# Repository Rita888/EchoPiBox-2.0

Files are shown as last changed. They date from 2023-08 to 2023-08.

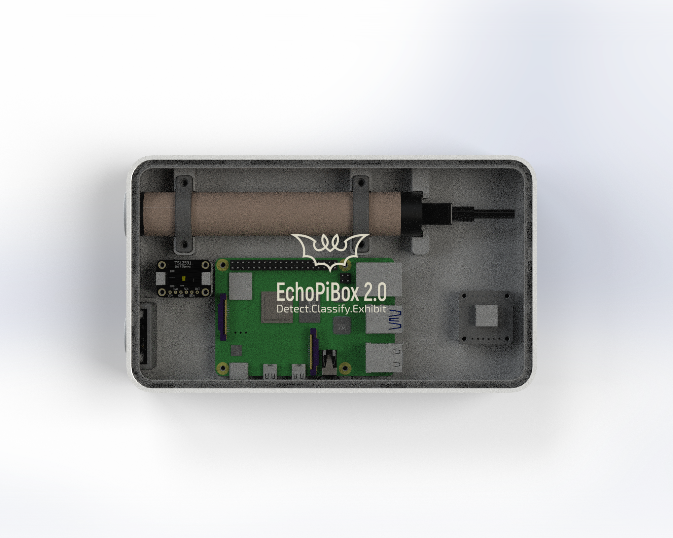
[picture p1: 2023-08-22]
Rita Enclosure V1/Render (2).png

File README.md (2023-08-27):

# EchoBoxPi2.0

Detect.Classify.Exhibit



EchoPiBox 2.0 Passive Acoustic Monitor: Detection, Species Identification Accuracy and Displaying Real Time Data.

MSc Connected Environments Dissertation by Margarita Smoldareva

Research Question: Can Raspberry Pi 4 host open-source machine learning model and three additional sensors to classify social bat calls plus display environmental variables along with accurate bat species in real time using Flutter App? 

This study is part of MSc Connected Environments programme which explores the use of a microprocessor and other hardware components wired together in a box with ability to detect and classify bats using open-source machine learning model developed by University College London (UCL). The aims and objectives of this thesis report are noted below that indicated the flow of the project. 

Detect
Aim: - Build a physical device (EchoPiBox 2.0) which allows bat calls detection. 
Objective: Set up Raspberry Pi 4, Ultramic, Temperature/Humidity and GPS Sensors to record environmental variables and bat calls. 

Classify
Aim: - Deploy Machine Learning Algorithm on EchoPiBox 2.0 and test its accuracy. 
Objective: Select and deploy the device across five sites based in England and Wales to test accuracy of classification of bat calls. 

Exhibit
Aim: - Display the Real Time Data
Objective: Using Flutter App display data collected by EchoPiBox 2.0 when deployed at any time.


Flowchart 1: Proposed Scheme for Deployment

UK bats and their importance 
Bat, being the sole flying mammal of the world is the most diverse specie on Earth. Except for Antarctica, they are found on every continent. 
In the United Kingdom, 18 different breeds of bat along with some vagrant visitors are found (Entwhistle et al., 2001). Bats are important creatures whose ecological 
roles as predator and prey have been postulated to regulate environmental and economic services including nutrient distribution, arthropod suppression, pollination, 
and biodiversity. For the purpose of foraging and roosting, the utilisation of different habitats by bats regulates nutrient dispersion and soil fertility to
facilitate dietary transfer within ecosystems from nutrient-rich locations to poor-nutrient regions (Buchler, 1975). Furthermore, bats serve as exceptional 
ecological indicators of habitat quality. Due to their mobility, ecological distribution, population trends, taxonomic stability, size, global distribution, 
and longevity, bats have great potential as bioindicators for contaminants and disturbance in the atmosphere (Kasso and Balakrishnan, 2013, 4). 

Similarly, tropical bats provide immense support as pollinators to national and local economies. The role of bats as a bioindicator taxa is highly essential to
evaluate climatic responses, loss of habitat, and insects’ population in a particular region enabling the researchers to reflect on forthcoming impacts and 
wider-scale changes on biodiversity.

Despite being an essential contributor to the environment and nature, bat populations have drastically declined in the United Kingdom. Due to a lack of substantial 
historical data on bat distribution and population sizes, it is hard to quantify the population decline. However, some common issues for bats' survival include poor 
management of their feeding habitats, roost sites, and lack of protection of hibernation sites (hibernacula) (Entwhistle, 7). Thus, the population of British bats
has shrunk notably and species conservation techniques and interventions are being studied and implemented to meet their habitat requirements (Hill and Greenaway, 2008).

Bat Conservation Trust (BCT, 2023) play a vital role in advocating for conservation, raising awareness, conducting research, and providing resources and guidance for 
individuals, communities, and professionals. 

Bioacoustics
Within the ecological realm, studying acoustic signals have been a renowned scientific method for investigating sound dispersion, reception, and production of different
mammals and birds (Wang and Bu, 2022, 250). To determine species abundance and bat activity, bioacoustics methods are used to extract essential information and data from
bats’ echolocation calls for conservation monitoring and biodiversity research (Ruiz et al., 2017). Bats are nocturnal mammals that utilise an echolocation system
(high-frequency calls) to picture and navigate their environment in the dark. The basic mechanism of echolocation is similar to sonar, where the returning echoes
are used to create a sonic picture of their surroundings. These ultrasonic calls are recorded and captured by ecologists to study bat activities in a certain area.
The bio sonar mechanism in bats serves as an acoustic imaging modality in real time (Simmons and Gaudette, 2012, 556). This mechanism enables bats to extract 
detailed information about their location as the auditory systems of bats are equipped with highly specialised neurons (Suga, 1990). In the life of echolocating bats,
bio-sonar provides a wide range of functionalities from finding food, navigating obstacles, and locating and flying through dangerous surroundings for example vegetation.

Acoustic detection of bat species includes recognition and observation of call patterns and design from sonograms of ultrasonic calls. However, the conventional manual 
identification of these calls requires a higher level of training and tend to be very time-consuming (Ruiz et al., 2017). The ultrasonic calls are the carriers of bats' 
information into the environment that are beneficial to explore population trends, activity patterns, specific-specie identification, and overall health of the 
environment (Gallacher et al., 2021). As per the study presented by Clement et al., (2014), the identification procedure includes a set library of calls of the target 
species, extraction of frequency and time data from call spectrograms, and lastly, the implementation of statistical technique to predict and analyze the identity of 
vocalizations captured during acoustic examination. Bioacoustics methods are noninvasive remote surveys that require less effort and hard work compared to labor-
intensive trapping and roost monitoring methods (Walters et al., 2013, 480). 

BAT DETECTORS ON THE MARKET

The utilisation of bat detectors in bat population conservation plays a crucial role to identify important foraging and roosting sites that ensure their survival. It is 
a battery-operated, handheld device that is used to capture and record ultrasonic bat calls. In the beginning, these detectors were intended as a DIY project that later 
evolved, becoming high-quality equipment for bat scientists and wildlife enthusiasts. The ultrasonic sounds produced by bats during their echolocation calls can be 
converted into audible audio with the help of a bat detector. The characteristics of these calls can be used to identify the bat species and nocturnal activities.

Song Meter Mini Bat

It is the lightest (290g), most affordable, and smallest (12.3 x 16.8 x 3.6 cm) commercially available audio recorder. It can process and record data for up to 30 nights 
(10 hours each) with 4 AA batteries. It is equipped with a built-in microphone offering identical quality to the SM4 mics. The recorder is Bluetooth enabled and the 
settings of the device can be easily accessed with the app. This detector comes equipped with a Kingston SDHC card, rechargeable batteries, and Masterlock Python Cable 
8417D (Nationwide Ecology Supplies, n.d).

Song Meter-SM4BAT-FS with SMM-U2

This particular bat detector is the most widely used full-spectrum static device that can survive in the field for a whole month with D-cell batteries. The entire 
detection system is enclosed in a polycarbonate rugged casing with weatherproof covers and mounting brackets. It has a pre-programmed schedule for effective bat surveys
and also enables customized schedules too. It has a single microphone recording channel that rates up to 16-bit 500 kHz.

MACHINE LEARNING IN BIOACOUSTICS 

BATCORDER
According to Fritsch and Bruckner (2014), a large amount of call recordings can be facilitated through software-based identification, especially for extensive acoustic
experiments that involve various collaborators. However, validation at the time of species classification may raise identification bias where more than one participant 
is present due to varying degrees of knowledge and experience. This could affect the quality of the data being analyzed, more specifically for species with difficult 
acoustic frequencies. Keeping this in view, the authors explained the working mechanism of the batcorder system where the automated classification of the species list 
can generate an unvalidated output of call sequences. The system of batcorder contains three main operable working units namely the batcorder, which is the recording 
device, bcAdmin, which is the visualization and administration software and lastly batIdent, which is the identification software. The acoustical properties during the 
survey are recorded, measured, and discerned by bcAdmin based on the minimum and maximum frequency and call length. These measurements are then transferred to batIdent 
for individual call identification. This part of the software utilizes Random Forest Algorithm for identification via R statistical software. Each call sequence is 
classified into different calls while the long sequences with many calls are further classified. Each call within the classification is assigned to more than one taxon,
resulting in unvalidated call sequences. In their study, Fritsch and Bruckner raised the concern to standardize the process of validation by harmonizing the results of
operators with different experiences. 

RANDOM FOREST ALGORITHM
In the study presented by Ruiz et al., (2017), a computational method for the automated detection and identification of bat species was proposed. Based on the 
echolocation mechanism, the authors aimed to perform an experiment in complex soundscapes of tropical ecosystems. The experiment involved a statistical voice activity
detector coupled with a supervised machine learning technique namely a random forest algorithm. The test was performed using a library of echolocation calls belonging
to 36 different species of neotropical bat. The research aimed to accurately identify and detect a diverse group of bat species within noisy and complex soundscapes 
from natural environments. Generally, to identify bat calls in ultrasonic frequency, the audio signal is represented in the range of time frequency. However, signal 
distortion (microphone gain) and background noises (including power lines, insects, electronic devices, and footsteps) are most likely to hinder signal detection from 
the area of inspection. Similarly, the authors also argued the effectiveness of spectrograms for bat call detection but ended up using VAD (voice activity detector)
technique. This technique is a model-based procedure that utilized speech processing to detect the absence or presence of speech. Also, a model-based approach for 
detection has fewer false positives compared to spectral peak detectors in spectrograms (Skowronski and Fenton, 2008). The result of the study showed that the random 
forest technique proved to be the most accurate machine learning algorithm for the acoustic identification of bat species among the five learning classifiers. 

CONVOLUTIONAL NEURAL NETWORK
Passive acoustic sensing as a way of monitoring and surveying anthropogenic impacts on wildlife and biodiversity has recently become a useful tool, specifically to 
quantify bat echolocation calls. As per the study presented by Mac Aodha et al., (2018), an open-source CNN (convolutional neural network) based pipeline was introduced
to detect search-phase, ultrasonic, and full spectrum calls generated by bats. The deep learning algorithms used by the authors were trained to collect ultrasonic audio
along road transects in Bulgaria and Romania by researchers in iBats program. The design of the CNN-based detector was tested against different commercial systems and 
algorithms on datasets recorded in different countries using varying sensors. The testing showed that the CNN-based detector has higher performance in terms of recall 
and precision of search-phase bat calls as compared to commercial systems. 

The researchers were successful to portray the automated and accurate search-phase detection of bat calls, specifically retrieved from a noisy audio recording. 
The deep learning-based pipeline allowed automatic monitoring and detection of bat species and populations. The system was further incorporated to cater to transparency
and progress for forthcoming systems. The CNN system was able to localize echolocation bat calls in recordings which was earlier a very difficult task in commercial 
systems, especially retrieving from noisy audio. 

BATDETECT2
Despite the fact that acoustic monitoring is a scalable and effective technique to assess the activities and patterns of bioindicator taxa, there exists a substantial 
amount of noise and distortion in the data. For this reason, it is important to use accurate tools that automatically detect the presence of the targeted specie.
As per Mac Aodha et al., (2022), in such scenarios, machine learning-based techniques have the maximum potential to yield optimal results, however,
to properly deploy the technique, expertise is required. In their study, the authors have proposed a novel approach for echolocation call detection 
namely BatDetect2. It is a deep learning-based pipeline that classifies and detects bat species by interpreting acoustic data. 
As per the authors, the outputs of BatDetect2 are interpretable as it allows direct indication of echolocation calls in terms of frequency and time. 
Furthermore, the temporal information from the surrounding is also utilised by BatDetect2 which maintain the computational efficiency at the time of deployment and 
improve its predictions. To enable researchers and practitioners to deploy, annotate and train the model, BatDetect2 contains open-source tools in the datasets.
The authors comprehensively tested the effectiveness of the model on five datasets, retrieved from four different geographical locations 
(Brazil, UK, Australia, and Mexico). For a 17 UK bat species dataset, the mean average was 0.88, which was visibly better than the 0.71 attained by the
conventional call extraction baseline method.

BAT POINT COUNTS
In their study, Darras et al., (2021) explored the promising results of electromagnetic energy to sample bat communities. According to the authors, the bat point counts 
technique is a novel sampling procedure that eradicates the shortcomings and sampling bias of conventional sampling techniques. The novel method involves a sampling rig
joined with a thermal scope for bat detection, a near-infrared camera for capturing the bat morphology, and an ultrasound recorder to collect echolocation calls. The 
bat point counts serve as a non-invasive, competitive, and promising novel tool that aids in observing bats’ behaviour in the environment without bias.  

RASPBERRY PI IN BIOACOUSTICS
The vast capabilities of the Raspberry Pi, including its ease of use, customisable hardware, and low cost make it a commendable research tool in the field of bat
detection and bioacoustics. Similarly, automatic recording of bat echolocation calls, vegetation structure, bat diversity, and population can be done using bat 
detectors made with Raspberry Pi technology (Jolles, 2021). For bioacoustics, Raspberry Pi is being readily used for audio recording to assess habitats, biodiversity,
and vocalizations of bats and birds. A Bioacoustics recorder named ‘SOLO’ was built by Whytock and Christie (2017), using a single board of Raspberry Pi that could 
record audio for straight 40 days being highly customizable and easy to use. Similarly, a bat survey on a derelict building in the UK was carried out using Raspberry Pi
technology and a simple ultrasonic mic (Whittaker, 2020). The system consisted of Raspberry Pi software, an ultrasonic mic, and an STM M0 processor. The recorded audio 
was sent to the software using bash language that received the data from Alsa driver software. With the help of this device, a team of bat enthusiasts was able to 
identify 9 different species of bat in the United Kingdom.

Similarly, with the use of a 384 kHz full spectrum recorder and Raspberry Pi Pico bat detector, sonic chirps of bats can be easily heard and recorded during their 
nocturnal activities (Horsey, 2023). The Pico bat detector processes the audio in real-time due to which live calls of bats’ echolocation can be heard. The time 
expansion mode in the detector is present to slow and transposed down the speed of the audio 16x and 4 octaves down respectively. Within the detector, the operational
amplifier and ultrasonic microphone are present that amplify and capture the bat calls which are sampled by Raspberry Pi. The functionality of the device resembles a 
full-spectrum recorder where 384 kHz ultrasonic audio can be saved to allow offline analysis as well. The LED display powered by Raspberry Pico’s PWM system provides an
analog display and speech synthesis feedback is present to pinpoint targeted bat calls and accurate detection of the frequency.

Bat Pi 4, a new, compact yet highly functional version of the bat detector has been introduced with an easy operational and configurational setting that is LAN enabled
and provides cloud technology that stores audio recordings for offline analysis (Raspberry Pi bat project, n.d). The recording from this detector is time-controlled 
with GPS support and an ultrasonic USB microphone to capture bat calls during their nocturnal activities.

LIGHT AND WEATHER CONDITIONS IMPACT ON BATS
With a rapid increase in the human population in urban areas, the landscape of the cities is constantly expanding posing various vicissitudes in ecosystems such as decreased habitat connectivity due to roads, buildings, and surface sealing concrete and variance in local climates (Voigt et al., 2020). All of these anthropogenic 
disturbances caused wildlife species to shift their urban habitats and environment. One of the most crucial anthropogenic stressors for bats is ALAN (artificial light
at night). Being nocturnal creatures, bats are designed to function more effectively during the nighttime. However, the physical and psychological cycle of bats is 
highly vulnerable to the adverse side effects of ALAN on their nocturnal activities. In some cases, during foraging some bats prefer ALAN sites but the majority of the 
evidence suggested that bats tend to bypass and avoid illuminated drinking sites, even foraging places and illuminated routes (Zeale et al., 2018). Voigt et al. 
analysed the spatial behavior of noctule bats with miniaturized GPS loggers to assess the habitat features of urban bats with respect to ALAN and found that the 
majority of the bats repelled and resisted flying across illuminated neighborhoods especially roads during foraging as the traffic noise was an additional repellant to
their natural habitat requirements. 

Supporting the aforementioned study, Laforge et al., (2019) presented a similar idea in their research where the authors proposed that light pollution can affect 
landscape connectivity and movements of the animals, especially in ever-evolving urban landscapes. Due to this, conservation interventions are constantly being employed
to reduce light during the night to help bats reconnect with the landscape. The authors utilized a species distribution model with random stratified sampling on Myotis 
daubentonii, Pipistrellus nathusii, and Eptesicus serotinus. The result of the study showed a positive response of light reduction for M. daubentonii and P. nathusii. 
Thus, the author recommended preventive measures for light reduction in urban planning to maintain sustainable habitat conditions for urban bats. 

Similarly, as per Cravens and Boyles (2019), the use of artificial lights in the city may induce disturbances for the wildlife community. The authors tested the 
differential impact of light pollution on insectivorous nocturnal bats using a physiological technique by measuring the blood metabolite (ß-hydroxybutyrate) of 6 
species of bats in unlit and lit conditions. Bat calls were also recorded acoustically to assess activity levels during the experiment. The results of the study 
suggested that only red bats were able to actively forage in lit conditions, while the rest of the specie avoided light. 

Apart from artificial light, weather conditions also pose alterations to bats living conditions and activities in terms of hibernation, life cycle, and prey 
availability (Mendes et al., 2017). Unfavorable weather situations like strong winds and heavy rain negatively affect bat activity. The ecological terrain selection of 
bats heavily relies on weather conditions, air temperature, and prey availability during site selection for their habitats. 

METHODOLOGY 

DETECT – BUILDING THE DEVICE 

The main component of a bat detector is a microphone which is able to detect echolocation emitted from the bats. The additional sensors provide more data which can influence bat species accuracy such as light sensitivity and location. 


Plate 1: Ultramic (NHBS, 2023)

The Ultramic is a fully digital USB ultrasound microphone with integrated digital to analog converter and an option of 192 kHz, 200kHz or 250kHz sampling rate.
The USB 2.0 port allows for easy connection to your PC or MAC and no driver installation is required.
Compact and versatile the Ultramic is a great option for use in the field or laboratory. Whilst most often used to record the ultrasonic signals of both bats and 
rodents it is equally useful for detection of high-frequency noises emitted by LCD screens, turbines and power adaptors.

Specification
* 192K, 200K or 250K sampling per second.
* True 16 bit resolution.
* Frequency range up to 100kHz - 125kHz.
* MEMS high sensitivity Surface Mount Wide-band Ultrasonic Acoustic Sensor.
* High quality and low noise analogue amplification.
* USB full speed port with a mini B USB connector.
* 32 bit 80MHz integrated microcontroller.
* Dimensions: 130mm length x 20mm diameter.
Available on https://www.nhbs.com/ultramic-usb-ultrasound-microphone

[
](https://thepihut.com/products/raspberry-pi-4-model-b?variant=20064052740158&src=raspberrypi
https://thepihut.com/products/adafruit-aht20-temperature-humidity-sensor-breakout-board (optional)
https://thepihut.com/products/adafruit-tsl2591-high-dynamic-range-digital-light-sensor (optional) 
https://thepihut.com/products/adafruit-mini-gps-pa1010d-uart-and-i2c-stemma-qt (optional)
Micro SD of minimum 256GB is recommended (64gb or more for software back up)
)https://thepihut.com/products/raspberry-pi-4-model-b?variant=20064052740158&src=raspberrypi
https://thepihut.com/products/adafruit-aht20-temperature-humidity-sensor-breakout-board (optional)
https://thepihut.com/products/adafruit-tsl2591-high-dynamic-range-digital-light-sensor (optional) 
https://thepihut.com/products/adafruit-mini-gps-pa1010d-uart-and-i2c-stemma-qt (optional)
Micro SD of minimum 256GB is recommended (64gb or more for software back up)


Plate 2: Diagram of connecting the components (Solidworks, 2023)


Plate 3: Diagram of connecting the remaining  components (Solidworks, 2023)


Plate 4: Connecting the wires (Fritzing, 2023)


Plate 5: Final EchoPiBox 2.0 (EPB) Hardware Assembly (Smoldareva, 2023)

CLASSIFY – IDENTIFICATION AND TESTING ACCURACY 

To classify bat social calls, open source BatDetect2 (Macaodha, 2023 ) model was used to build up on to produce Acoupi software . 
The Acoupi software utilises the code used to run the BatDetect2 algorithm. 
Raw data produced by Acoupi software in Raspberry Pi. 

For this project, series of sites were selected to include habitat complexity that would allow different bat species to be present to test the accuracy of detecting as 
many of UK bat species at possible. The Bat Conservation Trust (BCT, 2023) provides comprehensive guidelines for conducting bat surveys, ranging from preliminary
assessment, emergence/re-entry, transect and roost surveys.

Due to personal experience of undertaking diverse bat surveys over eight years, it was possible to select sites in England and Wales with known presence of bats. 
Five sites were of diverse habitats and surrounding landscapes as described later in this chapter. The surveyor holds Natural England Level 1 Bat Licence therefore 
permitted to use artificial light to identify bat species. 

The nocturnal bat surveys commenced 20 minutes prior to sunset and completed around 90 to 120 minutes after the sunset. In conjunction to EchoPiBox 2.0, Echo Meter 
Touch (EMT) Pro for iOS from used to then compare the species recorded. The recordings were later analysed using Wildlife Acoustics Software to verify bat calls 
recorded on EMT.  

Deployment Results



EXHIBIT – DISPLAY REAL TIME DATA ON FLUTTER APP

Once the data collected using EMT was analysed using Kaleidoscope Viewer for Bat Analysis (Wildlife Acoustics, 2023) it then compared to the data collected using 
EchoPiBox 2.0. The accuracy of the Acoupi detection was set to 60% therefore any bat calls with less than 59% would not be displayed on the app. 


Flow chart 2: Overall Detection, Classification and Display Flow Chart

DISCUSSION AND FURTHER RECOMMENDATIONS 

BUILDING THE EPB– The aim of this study was to include the hardware that will be used to correctly identify bat species while deployed in the wild. 
The ultramic and the sensors did not present any challenges during the deployment. The power source was not discussed in this project as the main aims were to build a 
working bat detector, test the accuracy of the BatDetect2 model and display real time data using flutter app. As this device can be used as a handheld detector as well
as a static detector, therefore deployed over series of nights, weeks, months or be permanently installed on a lamppost. For this study portable DC/AC Power Bank with 
99WH capacity was used as the surveys were lasting over two hours at each of the time. If these are to be used as static detector, different power source should be used
to accommodate the power consumption of the Raspberry Pi. 

It must be also noted that the sensors were not calibrated and not tested during this study therefore further testing is recommended. Although, the real time data was 
displayed on the app, the accuracy of data particularly was lux, temp/humidity sensors were not tested due to lack of time. The GPS location was out by 25 to 50m which 
is suitable for this study however if more precise location is needed, use of another sensor is recommended. 

Also to be noted that due to 11-12 hours deployment time, the environmental data recorded was insufficient to allow any analysis of these parameters to determine 
accuracy of bat species such as the light sensitive bat species (e.g. Brown Long-eared bat and Myotis sp.) Further assessment would allow lux sensor to determine 
likelihood of bat species present within the locality. 

SETTING UP THE EPB– The software element was the most challenging in this study and about 70 per cent of the time spent on the project was to set up the Raspberry pi 
and provide the code for the sensors due to non-engineering background. Hence the detailed guid was produced to allow fellow ecologists with non-engineering background 
to navigate through EchoPiBox 2.0 set up. 

BATDETECT2/ACOUPI were easy to install once the Raspberry Pi was set up. Several deployments were undertaken prior to conducting surveys away from home. The accuracy 
was tested and concluded that any detections above 60% will be displayed on the real time data stream and anything less than 59% will be discarded. It is recommended 
that further deployments and tests are carried out to conclude on the accuracy percentage as just over ten hours of recordings cannot be sufficient to conclude on the 
accuracy. It is also recommended to deploy in different locations to capture all 17 UK species as only 11 species were classified during this study. 

The raw data shown that 14 species were recorded on one night of deployment however once the accuracy was changed to 60% this number dropped to 6 species. 
The species  might be occupying that specific location however due to only two-hour deployment; these bat species might have been too far away to be detected accurately. 

CONNECTIVITY – During the deployment, to test if the EPB is switched on, personal smart phone hotspot and TeamViewer App was used. Once the Flutter App was build, 
Alcatel 8094T Android tablet was used for hotspot connection. The device can be used in the wild without connectivity however there is a risk that the automated (PM2) 
is not running therefore not recording the data. The app allows to test if the device is operating by displaying the real time data however another way of connectivity 
must be explored to allow other sources of connection such as Long Range Wide Area Network (LoRaWAN). This will enable long range communication with low power 
consumption, allowing appliactions requires remote and battery-operated devices to transmit data over relatively long distances. 

THERMAL CONSTRAINTS – Once the device was inside its 3D printed box, the temperature emitted from the Raspberry Pi started to influence the sensor. For further design 
improvements, the temperature/humidity sensor should be placed outside the device box to avoid the false data reading. 

STORAGE – For this project 64GB SD card was used at the initial stage and by the second night of deployment, it was noted that more storage is needed. The SD was backed 
up and cloned using ApplePiBaker Software (PiBaker, 2023) on varies occasions to allow 256GB SD to be the final operation SD card installed within the Raspberry Pi 4. 

RAM – The Raspberry Pi 4 which was used for this study had 8GB which is lower than the traditional desktop or laptop computers. Although, the real time data was 
displayed on the app, there is a slight delay and at the time of the write is was inconclusive if this issue was due to RAM or Firebase/iCloud limitations. 

BETTER IOT – To make this device more sustainable, it is advised to use the assessment tool provided by the Better IOT. This tool was developed to address some of the
pressing issue in the early stages of development to include: “privacy, openness, interoperability, lifecycle, permissions, transparency, data governance and security”.
(BetterIOT, 2023). 

CONCLUSION 

This study had three aims and objectives: Detect, Classify and Exhibit, as stated at the start of this document. The physical device has all the hardware components 
needed to start recording bat calls as well as additional sensors that could impact on presence of bats such as temperature, artificial light and the location. 
To classify the bat calls collected, open-source machine learning Acoupi software (stemmed from BatDetect2 model) was installed on Raspberry Pi. 

The device was installed over 10 hours, approximately 2 hours at each of five different locations in England and Wales to detect as many bat species as possible. 
In total 11 species were recorded during deployment and the accuracy of open-source model was concluded to be precise. Due to Ultramic is very sensitive and many
misclassifications were recorded and the accuracy of the detection was then coded to 60% which reduced the species recorded from 14 to 11. 

The data collected was then sent to iCloud (Firebase) which then allowed the real time data to be displayed on the EchoPibox 2.0 Flutter App. There was a slight delay
of several seconds in displaying the data depending on its connectivity to WiFi or Mobile Hotspot. 

Overall, the study was successful however the report highlighted several improvements and recommendations in the discussion section to include power supply, calibrating
the sensors, connecting to stable data transmitting network, redesigning the enclosure box to be more robust and complaint with International Protection Rating (IPR). 
Lastly, it is also advisable to use Better IOT assessment tool to allow the device to be in line with sustainability. 

Applepi-Baker v2 for Raspberry Pi. Tweaking4All. (https://www.tweaking4all.com/software/macosx-software/applepi-baker-v2/ Accessed on 20th July 2023
Bat Conservation Trust. Guidance for professionals. (https://www.bats.org.uk/resources/guidance-for-professionals) Accessed on 10th May 2023

Better IOT. Making Good Design Actionable. (https://betteriot.wordpress.com) accessed on 25th August 2023 

Buchler, E. R. (1975). Food transit time in Myotis lucifugus Chiroptera: Vespertilionidae. Journal of Mammalogy, 56(1), 252-255.

Clement, M.J., Murray, K.L., Solick, D.I. and Gruver, J.C., 2014. The effect of call libraries and acoustic filters on the identification of bat echolocation. 
Ecology and evolution, 4(17), pp.3482-3493.

Cravens, Z.M. and Boyles, J.G., 2019. Illuminating the physiological implications of artificial light on an insectivorous bat community. Oecologia, 189, pp.69-77.

Darras, K.F.A., Yusti, E., Huang, J.C.C., Zemp, D.C., Kartono, A.P. and Wanger, T.C., 2021. Bat point counts: A novel sampling method shines light on flying bat
communities. Ecology and Evolution, 11(23), pp.17179-17190.

Entwhistle, A.C., Harris, S., Hutson, A.M., Walsh, A., Gibson, S.D., Hepburn, I. and Johnston, J., 2001. Habitat management for bats-a guide for land managers, land 
owners and their advisors.

Fritsch, G. and Bruckner, A., 2014. Operator bias in software‐aided bat call identification. Ecology and evolution, 4(13), pp.2703-2713.

Gallacher, S., Wilson, D., Fairbrass, A., Turmukhambetov, D., Firman, M., Kreitmayer, S., Mac Aodha, O., Brostow, G. and Jones, K., 2021. Shazam for bats: 
Internet of Things for continuous real‐time biodiversity monitoring. IET Smart Cities, 3(3), pp.171-183.

Hill, D. A., & Greenaway, F. (2008). Conservation of bats in British woodlands. British Wildlife, 19(3), 161.

Horsey, J. (2023, July 17). Listen to bats using the raspberry Pi Pico bat detector. Geeky Gadgets. https://www.geeky-gadgets.com/raspberry-pi-bat-detector-17-07-2023/

Jolles, J.W., 2021. Broad‐scale applications of the Raspberry Pi: A review and guide for biologists. Methods in Ecology and Evolution, 12(9), pp.1562-1579.

Kasso, M., & Balakrishnan, M. (2013). Ecological and economic importance of bats (Order Chiroptera). Isrn Biodiversity, 2013, 1-9.
Laforge, A., Pauwels, J., Faure, B., Bas, Y., Kerbiriou, C., Fonderflick, J. and Besnard, A., 2019. Reducing light pollution improves connectivity for bats in urban
landscapes. Landscape Ecology, 34, pp.793-809.

Mac Aodha, O., Gibb, R., Barlow, K.E., Browning, E., Firman, M., Freeman, R., Harder, B., Kinsey, L., Mead, G.R., Newson, S.E. and Pandourski, I., 2018. 
Bat detective—Deep learning tools for bat acoustic signal detection. PLoS computational biology, 14(3), p.e1005995.

Mac Aodha, O., Martinez Balvanera, S., Damstra, E., Cooke, M., Eichinski, P., Browning, E., Barataud, M., Boughey, K., Coles, R., Giacomini, G. 
and Mac Swiney G, M.C., 2022. Towards a General Approach for Bat Echolocation Detection and Classification. bioRxiv, pp.2022-12.

Mendes, E.S., Fonseca, C., Marques, S.F., Maia, D. and Ramos Pereira, M.J., 2017. Bat richness and activity in heterogeneous landscapes: guild-specific and scale-dependent?. Landscape ecology, 32, pp.295-311.

Nationwide Ecology Supplies. Bat Detectors. https://www.wildcare.co.uk/media/amasty/amfile/attach/r7DGJpG7YFh6ydqaKHuKLH1QFbJUxTKa.pdf (accessed on 11th August 2023)

Raspberry Pi bat project. (n.d.). Raspberry Pi Bat Projekt. https://www.bat-pi.eu/EN/index-EN.html

Ruiz, A.T., Jung, K., Tschapka, M., Schwenker, F. and Palm, G., 2017. Automated identification method for detection and classification of neotropical bats.

Simmons, J.A. and Gaudette, J.E., 2012. Biosonar echo processing by frequency-modulated bats. IET Radar, Sonar & Navigation, 6(6), pp.556-565.

Skowronski, M.D. and Fenton, M.B., 2008. Model-based automated detection of echolocation calls using the link detector. The Journal of the Acoustical Society of America, 124(1), pp.328-336.

Suga, N., 1990. Biosonar and neural computation in bats. Scientific American, 262(6), pp.60-71.

Voigt, C.C., Scholl, J.M., Bauer, J., Teige, T., Yovel, Y., Kramer-Schadt, S. and Gras, P., 2020. Movement responses of common noctule bats to the illuminated urban landscape. Landscape Ecology, 35, pp.189-201.

Walters, C.L., Collen, A., Lucas, T., Mroz, K., Sayer, C.A. and Jones, K.E., 2013. Challenges of using bioacoustics to globally monitor bats. Bat evolution, ecology, and conservation, pp.479-499.

Wang, J. and Bu, Y., 2022. Internet of Things‐based smart insect monitoring system using a deep neural network. IET Networks, 11(6), pp.245-256.

Whittaker, A. (2020, October 16). Ultrasonically detect bats with raspberry Pi. Raspberry Pi.
https://www.raspberrypi.com/news/ultrasonically-detect-bats-with-raspberry-pi/ 

Whytock, R.C. and Christie, J., 2017. Solo: an open source, customizable and inexpensive audio recorder for bioacoustic research. 
Methods in Ecology and Evolution, 8(3), pp.308-312.

Zeale, M.R., Stone, E.L., Zeale, E., Browne, W.J., Harris, S. and Jones, G., 2018. 
Experimentally manipulating light spectra reveals the importance of dark corridors for commuting bats. Global Change Biology, 24(12), pp.5909-5918.

References for Codes (Excluding BatDecect2/Acoupi – noted as footnotes on page 18) 

Temperature/Humidity Sensor: https://github.com/adafruit/Adafruit_CircuitPython_SHT4x

Lux Sensor: https://github.com/adafruit/Adafruit_CircuitPython_TSL2591

GPS Sensor: https://github.com/adafruit/Adafruit_CircuitPython_GPS

Automated Process: https://github.com/Unitech/pm2

Firebase API for Flutter App: https://github.com/thisbejim/Pyrebase

The following codes were used for bat call data analysis recorded only by EchoPiBox 2.0 

https://github.com/pandas-dev/pandas

https://github.com/numpy/numpy

https://github.com/plotly/plotly.py

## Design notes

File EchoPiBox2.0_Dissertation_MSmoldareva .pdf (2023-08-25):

### TITLE:

EchoPiBox 2.0: Passive Acoustic Monitor - Detection, Species Identification Accuracy and Displaying Real Time Data.

https://github.com/Rita888/EchoPiBox-2.0

https://github.com/Rita888/EchoPiBox-2.0-app

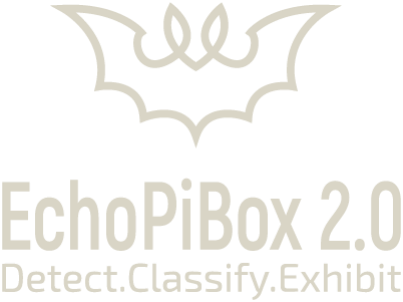
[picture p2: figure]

EchoPiBox 2.0 | Margarita Smoldareva 712285
25th August 2023 | MSc Connected Environments, UCL | 2

## TABLE OF CONTENTS

Title: | 1
Research Question: | 3
Introduction | 3
UK bats and their importance | 5
Bioacoustics | 7
Bat detectors on the market | 8
Machine Learning in Bioacoustics | 9
Batcorder | 9
Random Forest Algorithm | 9
Convolutional Neural Network | 10
BatDetect2 | 10
Bat Point Counts | 12
Raspberry Pi in Bioacoustics | 12
Light and Weather Conditions Impact on Bats | 13
Methodology | 14
Detect – Building the Device | 14
Classify – Identification and Testing Accuracy | 18
Deployment Results | 20
Exhibit – Display Real Time Data on Flutter App | 32
Discussion and Further Recommendations | 36
Building the EPB | 36
Setting up the EPB | 36
BatDetect2/Acoupi | 36
Connectivity | 37
Thermal Constraints | 37
Storage | 37
RAM | 37
Conclusion | 37
References | 38

### RESEARCH QUESTION:

Can Raspberry Pi 4 host open-source machine learning model and three additional sensors to classify social bat calls plus display environmental variables along with accurate bat species in real time using Flutter App?

### INTRODUCTION

This study is part of MSc Connected Environments programme which explores the use of a microprocessor and other hardware components wired together in a box with ability to detect and classify bats using open-source machine learning model developed by University College London (UCL). The aims and objectives of this thesis report are noted below that indicated the flow of the project.

Detect

Aim: - Build a physical device (EchoPiBox 2.0) which allows bat calls detection.

Objective: Set up Raspberry Pi 4, Ultramic, Temperature/Humidity and GPS Sensors to record environmental variables and bat calls.

Classify

Aim: - Deploy Machine Learning Algorithm on EchoPiBox 2.0 and test its accuracy.

Objective: Select and deploy the device across five sites based in England and Wales to test accuracy of classification of bat calls.

Exhibit

Aim: - Display the Real Time Data

Objective: Using Flutter App display data collected by EchoPiBox 2.0 when deployed at any time.

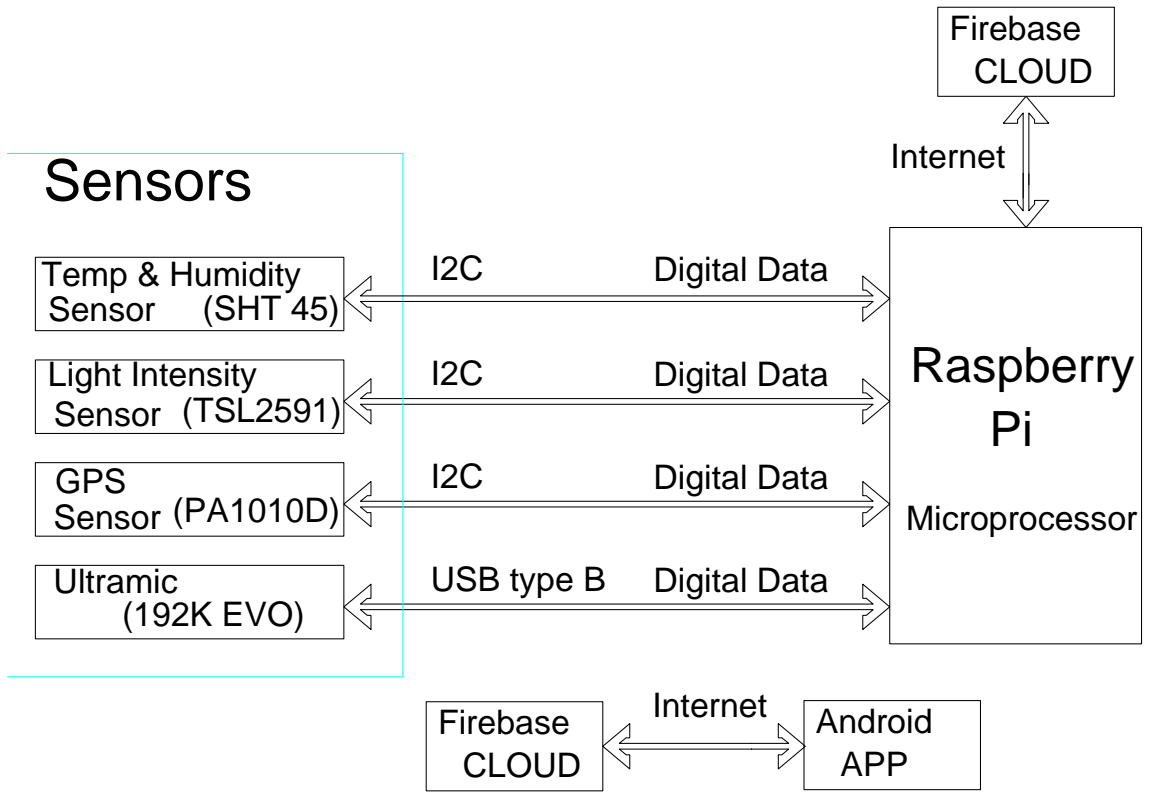
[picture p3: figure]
Raspberry Pi; Microprocessor; (SHT 45); Temp & Humidity Sensor; (TSL2591); Light Intensity Sensor; CLOUD; Firebase; Sensors; Internet; GPS Sensor; (192K EVO); Ultramic; USB type B; Digital Data; APP; Android

Flowchart 1: Proposed Scheme for Deployment

UK BATS AND THEIR IMPORTANCE

Bat, being the sole flying mammal of the world is the most diverse specie on Earth. Except for Antarctica, they are found on every continent. In the United Kingdom, 18 different breeds of bat along with some vagrant visitors are found (Entwhistle et al., 2001). Bats are important creatures whose ecological roles as predator and prey have been postulated to regulate environmental and economic services including nutrient distribution, arthropod suppression, pollination, and biodiversity. For the purpose of foraging and roosting, the utilisation of different habitats by bats regulates nutrient dispersion and soil fertility to facilitate dietary transfer within ecosystems from nutrient-rich locations to poor-nutrient regions (Buchler, 1975). Furthermore, bats serve as exceptional ecological indicators of habitat quality. Due to their mobility, ecological distribution, population trends, taxonomic stability, size, global distribution, and longevity, bats have great potential as bioindicators for contaminants and disturbance in the atmosphere (Kasso and Balakrishnan, 2013, 4).

Similarly, tropical bats provide immense support as pollinators to national and local economies. The role of bats as a bioindicator taxa is highly essential to evaluate climatic responses, loss of habitat, and insects’ population in a particular region enabling the researchers to reflect on forthcoming impacts and wider-scale changes on biodiversity.

Despite being an essential contributor to the environment and nature, bat populations have drastically declined in the United Kingdom. Due to a lack of substantial historical data on bat distribution and population sizes, it is hard to quantify the population decline. However, some common issues for bats' survival include poor management of their feeding habitats, roost sites, and lack of protection of hibernation sites (hibernacula) (Entwhistle, 7). Thus, the population of British bats has shrunk notably and species conservation techniques and interventions are being studied and implemented to meet their habitat requirements (Hill and Greenaway, 2008).

Bat Conservation Trust (BCT, 2023) play a vital role in advocating for conservation, raising awareness, conducting research, and providing resources and guidance for individuals, communities, and professionals.

Table 1: UK Bat Species (BCT, 2023)

| Common name | Scientific name
1 | Alcathoe Bat | Myotis alcathoe
2 | Barbastelle | Barbastella barbastellus
3 | Bechstein’s bat | Myotis bechsteinii
4 | Brandt’s bat | Myotis brantii
5 | Brown long-eared bat | Plecotus auratus
6 | Common Pipistrelle | Pipistrellus pipistrellus
7 | Daubenton’s bat | Myotis daubentonii
8 | Greater Horseshoe bat | Rhinolophus ferrumequinum
9 | Grey long-eared bat | Plecotus austriacus
10 | Leisler’s bat | Nyctalus leisleri
11 | Lesser horseshoe bat | Rhinolophus hipposideros
12 | Nathusius’ pipistrelle | Pipistrellus nathusii
13 | Natterer’s bat | Myotis nattereri
14 | Noctule | Nyctalus noctule
15 | Serotine | Eptesicus serotinus
16 | Soprano pipistrelle | Pipistrellus pygmaeus
17 | Whiskered bat | Myotis mystacinus
18 Greater mouse-eared bat (travelling species and | occasional visitors) | Myotis myotis

The United Kingdom has a strong domestic and international legislation.

Wildlife and Countryside Act 1981 (as amended): | In the UK, all bat species and their roosts are legally protected under the Wildlife and Countryside Act 1981 (WCA). This legislation makes it illegal to intentionally kill, injure, capture, or disturb bats, as well as to damage or destroy their roosts. This protection extends to their breeding and resting places. The act covers all bat species found in the UK.
Conservation of Habitats and Species Regulations 2017: | These regulations implement the European Union's Habitats Directive in the UK. Bats are included in the list of protected species, and their habitats are protected under this legislation.
Natural England, Natural Resources Wales, Scottish Natural Heritage, and Northern Ireland Environment Agency: | These are the responsible bodies in each respective UK nation for overseeing the protection and conservation of wildlife, including bats. They provide guidance, issue licenses for certain activities that might otherwise be prohibited, and enforce legal protections.

Table 2: Bat Protection Legislation

BIOACOUSTICS

Within the ecological realm, studying acoustic signals have been a renowned scientific method for investigating sound dispersion, reception, and production of different mammals and birds (Wang and Bu, 2022, 250). To determine species abundance and bat activity, bioacoustics methods are used to extract essential information and data from bats’ echolocation calls for conservation monitoring and biodiversity research (Ruiz et al., 2017). Bats are nocturnal mammals that utilise an echolocation system (high-frequency calls) to picture and navigate their environment in the dark. The basic mechanism of echolocation is similar to sonar, where the returning echoes are used to create a sonic picture of their surroundings. These ultrasonic calls are recorded and captured by ecologists to study bat activities in a certain area. The bio sonar mechanism in bats serves as an acoustic imaging modality in real time (Simmons and Gaudette, 2012, 556). This mechanism enables bats to extract detailed information about their location as the auditory systems of bats are equipped with highly specialised neurons (Suga, 1990). In the life of echolocating bats, bio-sonar provides a wide range of functionalities from finding food, navigating obstacles, and locating and flying through dangerous surroundings for example vegetation.

Acoustic detection of bat species includes recognition and observation of call patterns and design from sonograms of ultrasonic calls. However, the conventional manual identification of these calls requires a higher level of training and tend to be very time-consuming (Ruiz et al., 2017). The ultrasonic calls are the carriers of bats' information into the environment that are beneficial to explore population trends, activity patterns, specific-specie identification, and overall health of the environment (Gallacher et al., 2021). As per the study presented by Clement et al., (2014), the identification procedure includes a set library of calls of the target species, extraction of frequency and time data from call spectrograms, and lastly, the implementation of statistical technique to predict and analyze the identity of vocalizations captured during acoustic examination. Bioacoustics methods are noninvasive remote surveys that require less effort and hard work compared to labor-intensive trapping and roost monitoring methods (Walters et al., 2013, 480).

BAT DETECTORS ON THE MARKET

The utilisation of bat detectors in bat population conservation plays a crucial role to identify important foraging and roosting sites that ensure their survival. It is a battery-operated, handheld device that is used to capture and record ultrasonic bat calls. In the beginning, these detectors were intended as a DIY project that later evolved, becoming high-quality equipment for bat scientists and wildlife enthusiasts. The ultrasonic sounds produced by bats during their echolocation calls can be converted into audible audio with the help of a bat detector. The characteristics of these calls can be used to identify the bat species and nocturnal activities.

Song Meter Mini Bat

It is the lightest (290g), most affordable, and smallest (12.3 x 16.8 x 3.6 cm) commercially available audio recorder. It can process and record data for up to 30 nights (10 hours each) with 4 AA batteries. It is equipped with a built-in microphone offering identical quality to the SM4 mics. The recorder is Bluetooth enabled and the settings of the device can be easily accessed with the app. This detector comes equipped with a Kingston SDHC card, rechargeable batteries, and Masterlock Python Cable 8417D (Nationwide Ecology Supplies, n.d).

Song Meter-SM4BAT-FS with SMM-U2

This particular bat detector is the most widely used full-spectrum static device that can survive in the field for a whole month with D-cell batteries. The entire detection system is enclosed in a polycarbonate rugged casing with weatherproof covers and mounting brackets. It has a pre-programmed schedule for effective bat surveys and also enables customized schedules too. It has a single microphone recording channel that rates up to 16-bit 500 kHz.

MACHINE LEARNING IN BIOACOUSTICS

BATCORDER

According to Fritsch and Bruckner (2014), a large amount of call recordings can be facilitated through software-based identification, especially for extensive acoustic experiments that involve various collaborators. However, validation at the time of species classification may raise identification bias where more than one participant is present due to varying degrees of knowledge and experience. This could affect the quality of the data being analyzed, more specifically for species with difficult acoustic frequencies. Keeping this in view, the authors explained the working mechanism of the batcorder system where the automated classification of the species list can generate an unvalidated output of call sequences. The system of batcorder contains three main operable working units namely the batcorder, which is the recording device, bcAdmin, which is the visualization and administration software and lastly batIdent, which is the identification software. The acoustical properties during the survey are recorded, measured, and discerned by bcAdmin based on the minimum and maximum frequency and call length. These measurements are then transferred to batIdent for individual call identification. This part of the software utilizes Random Forest Algorithm for identification via R statistical software. Each call sequence is classified into different calls while the long sequences with many calls are further classified. Each call within the classification is assigned to more than one taxon, resulting in unvalidated call sequences. In their study, Fritsch and Bruckner raised the concern to standardize the process of validation by harmonizing the results of operators with different experiences.

RANDOM FOREST ALGORITHM

In the study presented by Ruiz et al., (2017), a computational method for the automated detection and identification of bat species was proposed. Based on the echolocation mechanism, the authors aimed to perform an experiment in complex soundscapes of tropical ecosystems. The experiment involved a statistical voice activity detector coupled with a supervised machine learning technique namely a random forest algorithm. The test was performed using a library of echolocation calls belonging to 36 different species of neotropical bat. The research aimed to accurately identify and detect a diverse group of bat species within noisy and complex soundscapes from natural environments. Generally, to identify bat calls in ultrasonic frequency, the audio signal is represented in the range of time frequency. However, signal distortion (microphone gain) and background noises (including power lines, insects, electronic devices, and footsteps) are most likely to hinder signal detection from the area of inspection. Similarly, the authors also argued the effectiveness of spectrograms for bat call detection but ended up using VAD (voice activity detector) technique. This technique is a model-based procedure that utilized speech processing to detect the absence or presence of speech. Also, a model-based approach for detection has fewer false positives compared to spectral peak detectors in spectrograms (Skowronski and Fenton, 2008). The result of the study showed that the random forest technique proved to be the most accurate machine learning algorithm for the acoustic identification of bat species among the five learning classifiers.

CONVOLUTIONAL NEURAL NETWORK

Passive acoustic sensing as a way of monitoring and surveying anthropogenic impacts on wildlife and biodiversity has recently become a useful tool, specifically to quantify bat echolocation calls. As per the study presented by Mac Aodha et al., (2018), an open-source CNN (convolutional neural network) based pipeline was introduced to detect search-phase, ultrasonic, and full spectrum calls generated by bats. The deep learning algorithms used by the authors were trained to collect ultrasonic audio along road transects in Bulgaria and Romania by researchers in iBats program. The design of the CNN-based detector was tested against different commercial systems and algorithms on datasets recorded in different countries using varying sensors. The testing showed that the CNN-based detector has higher performance in terms of recall and precision of search-phase bat calls as compared to commercial systems.

The researchers were successful to portray the automated and accurate search-phase detection of bat calls, specifically retrieved from a noisy audio recording. The deep learning-based pipeline allowed automatic monitoring and detection of bat species and populations. The system was further incorporated to cater to transparency and progress for forthcoming systems. The CNN system was able to localize echolocation bat calls in recordings which was earlier a very difficult task in commercial systems, especially retrieving from noisy audio.

BATDETECT2

Despite the fact that acoustic monitoring is a scalable and effective technique to assess the activities and patterns of bioindicator taxa, there exists a substantial amount of noise and distortion in the data. For this reason, it is important to use accurate tools that automatically detect the presence of the targeted specie. As per Mac Aodha et al., (2022), in such scenarios, machine learning-based techniques have the maximum potential to yield optimal results, however, to properly deploy the technique, expertise is required. In their study, the authors have proposed a novel approach for echolocation call detection namely BatDetect2. It is a deep learning-based pipeline that classifies and detects bat species by interpreting acoustic data.

As per the authors, the outputs of BatDetect2 are interpretable as it allows direct indication of echolocation calls in terms of frequency and time. Furthermore, the temporal information from the surrounding is also utilised by BatDetect2 which maintain the computational efficiency at the time of deployment and improve its predictions. To enable researchers and practitioners to deploy, annotate and train the model, BatDetect2 contains open-source tools in the datasets. The authors comprehensively tested the effectiveness of the model on five datasets, retrieved from four different geographical locations (Brazil, UK, Australia, and Mexico). For a 17 UK bat species dataset, the mean average was 0.88, which was visibly better than the 0.71 attained by the conventional call extraction baseline method.

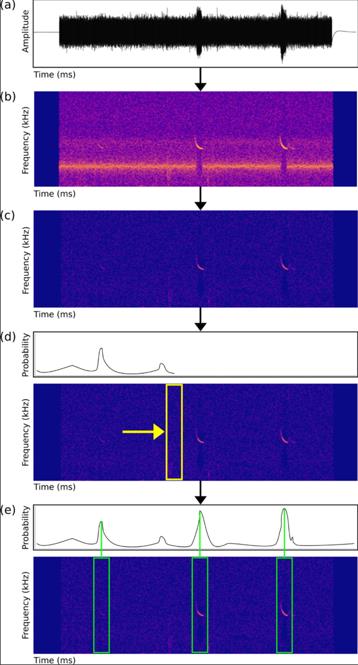
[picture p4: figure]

Fig 1. Detection pipeline for search-phase bat echolocation calls from the initial Bat Detect Model developed in 2018 (Mac Aodha et al., 2018)

(a) Raw audio files are converted into a spectrogram using a Fast Fourier Transform (b). Files are de-noised (c), and a sliding window Convolutional Neural Network (CNN) classifier (d, yellow box) produces a probability for each time step. Individual call detection probabilities using non-maximum suppression are produced (e, green boxes), and the time in file of each prediction along with the classifier probability are exported as text files.

BAT POINT COUNTS

In their study, Darras et al., (2021) explored the promising results of electromagnetic energy to sample bat communities. According to the authors, the bat point counts technique is a novel sampling procedure that eradicates the shortcomings and sampling bias of conventional sampling techniques. The novel method involves a sampling rig joined with a thermal scope for bat detection, a near-infrared camera for capturing the bat morphology, and an ultrasound recorder to collect echolocation calls. The bat point counts serve as a non-invasive, competitive, and promising novel tool that aids in observing bats’ behaviour in the environment without bias.

RASPBERRY PI IN BIOACOUSTICS

The vast capabilities of the Raspberry Pi, including its ease of use, customisable hardware, and low cost make it a commendable research tool in the field of bat detection and bioacoustics. Similarly, automatic recording of bat echolocation calls, vegetation structure, bat diversity, and population can be done using bat detectors made with Raspberry Pi technology (Jolles, 2021). For bioacoustics, Raspberry Pi is being readily used for audio recording to assess habitats, biodiversity, and vocalizations of bats and birds. A Bioacoustics recorder named ‘SOLO’ was built by Whytock and Christie (2017), using a single board of Raspberry Pi that could record audio for straight 40 days being highly customizable and easy to use. Similarly, a bat survey on a derelict building in the UK was carried out using Raspberry Pi technology and a simple ultrasonic mic (Whittaker, 2020). The system consisted of Raspberry Pi software, an ultrasonic mic, and an STM M0 processor. The recorded audio was sent to the software using bash language that received the data from Alsa driver software. With the help of this device, a team of bat enthusiasts was able to identify 9 different species of bat in the United Kingdom.

Similarly, with the use of a 384 kHz full spectrum recorder and Raspberry Pi Pico bat detector, sonic chirps of bats can be easily heard and recorded during their nocturnal activities (Horsey, 2023). The Pico bat detector processes the audio in real-time due to which live calls of bats’ echolocation can be heard. The time expansion mode in the detector is present to slow and transposed down the speed of the audio 16x and 4 octaves down respectively. Within the detector, the operational amplifier and ultrasonic microphone are present that amplify and capture the bat calls which are sampled by Raspberry Pi. The functionality of the device resembles a full-spectrum recorder where 384 kHz ultrasonic audio can be saved to allow offline analysis as well. The LED display powered by Raspberry Pico’s PWM system provides an analog display and speech synthesis feedback is present to pinpoint targeted bat calls and accurate detection of the frequency.

Bat Pi 4, a new, compact yet highly functional version of the bat detector has been introduced with an easy operational and configurational setting that is LAN enabled and provides cloud technology that stores audio recordings for offline analysis (Raspberry Pi bat project, n.d). The recording from this detector is time-controlled with GPS support and an ultrasonic USB microphone to capture bat calls during their nocturnal activities.

LIGHT AND WEATHER CONDITIONS IMPACT ON BATS

With a rapid increase in the human population in urban areas, the landscape of the cities is constantly expanding posing various vicissitudes in ecosystems such as decreased habitat connectivity due to roads, buildings, and surface sealing concrete and variance in local climates (Voigt et al., 2020). All of these anthropogenic disturbances caused wildlife species to shift their urban habitats and environment. One of the most crucial anthropogenic stressors for bats is ALAN (artificial light at night). Being nocturnal creatures, bats are designed to function more effectively during the nighttime. However, the physical and psychological cycle of bats is highly vulnerable to the adverse side effects of ALAN on their nocturnal activities. In some cases, during foraging some bats prefer ALAN sites but the majority of the evidence suggested that bats tend to bypass and avoid illuminated drinking sites, even foraging places and illuminated routes (Zeale et al., 2018). Voigt et al. analysed the spatial behavior of noctule bats with miniaturized GPS loggers to assess the habitat features of urban bats with respect to ALAN and found that the majority of the bats repelled and resisted flying across illuminated neighborhoods especially roads during foraging as the traffic noise was an additional repellant to their natural habitat requirements.

Supporting the aforementioned study, Laforge et al., (2019) presented a similar idea in their research where the authors proposed that light pollution can affect landscape connectivity and movements of the animals, especially in ever-evolving urban landscapes. Due to this, conservation interventions are constantly being employed to reduce light during the night to help bats reconnect with the landscape. The authors utilized a species distribution model with random stratified sampling on Myotis daubentonii, Pipistrellus nathusii, and Eptesicus serotinus. The result of the study showed a positive response of light reduction for M. daubentonii and P. nathusii. Thus, the author recommended preventive measures for light reduction in urban planning to maintain sustainable habitat conditions for urban bats.

Similarly, as per Cravens and Boyles (2019), the use of artificial lights in the city may induce disturbances for the wildlife community. The authors tested the differential impact of light pollution on insectivorous nocturnal bats using a physiological technique by measuring the blood metabolite (ß-hydroxybutyrate) of 6 species of bats in unlit and lit conditions. Bat calls were also recorded acoustically to assess activity levels during the experiment. The results of the study suggested that only red bats were able to actively forage in lit conditions, while the rest of the specie avoided light.

Apart from artificial light, weather conditions also pose alterations to bats living conditions and activities in terms of hibernation, life cycle, and prey availability (Mendes et al., 2017). Unfavorable weather situations like strong winds and heavy rain negatively affect bat activity. The ecological terrain selection of bats heavily relies on weather conditions, air temperature, and prey availability during site selection for their habitats.

### METHODOLOGY

DETECT – BUILDING THE DEVICE

The main component of a bat detector is a microphone which is able to detect echolocation emitted from the bats. The additional sensors provide more data which can influence bat species accuracy such as light sensitivity and location.

Plate 1: Ultramic (NHBS, 2023)

The Ultramic is a fully digital USB ultrasound microphone with integrated digital to analog converter and an option of 192 kHz, 200kHz or 250kHz sampling rate. The USB 2.0 port allows for easy connection to your PC or MAC and no driver installation is required.

Compact and versatile the Ultramic is a great option for use in the field or laboratory. Whilst most often used to record the ultrasonic signals of both bats and rodents it is equally useful for detection of high-frequency noises emitted by LCD screens, turbines and power adaptors.

Specification

* 192K, 200K or 250K sampling per second.

* True 16 bit resolution.

* Frequency range up to 100kHz - 125kHz.

* MEMS high sensitivity Surface Mount Wide-band Ultrasonic Acoustic Sensor.

* High quality and low noise analogue amplification.

* USB full speed port with a mini B USB connector.

* 32 bit 80MHz integrated microcontroller.

* Dimensions: 130mm length x 20mm diameter.

Available on https://www.nhbs.com/ultramic-usb-ultrasound-microphonehttps://thepihut.com/products/raspberry-pi-4-model-b?variant=20064052740158&src=raspberrypi

https://thepihut.com/products/adafruit-aht20-temperature-humidity-sensor-breakout-board (optional)

https://thepihut.com/products/adafruit-tsl2591-high-dynamic-range-digital-light-sensor (optional)

https://thepihut.com/products/adafruit-mini-gps-pa1010d-uart-and-i2c-stemma-qt (optional)

Micro SD of minimum 256GB is recommended (64gb or more for software back up)

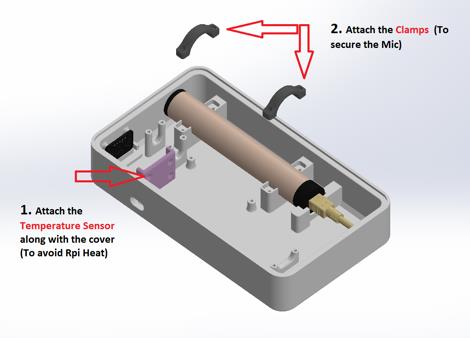
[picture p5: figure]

Plate 2: Diagram of connecting the components (Solidworks, 2023)

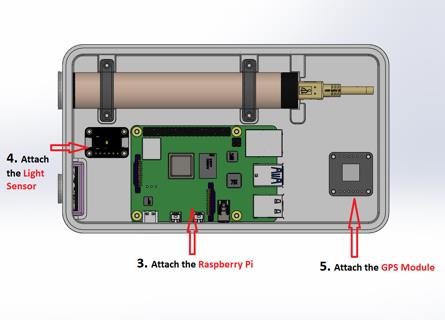
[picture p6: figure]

Plate 3: Diagram of connecting the remaining components (Solidworks, 2023)

Initial Enclosure Design:

https://github.com/Rita888/EchoPiBox-2.0/tree/main/Rita%20Enclosure%20V1

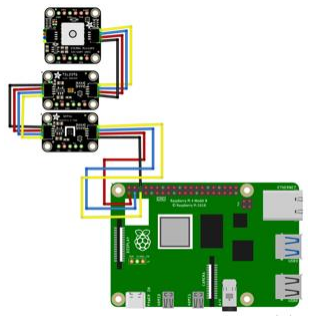
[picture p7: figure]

Plate 4: Connecting the wires (Fritzing, 2023)

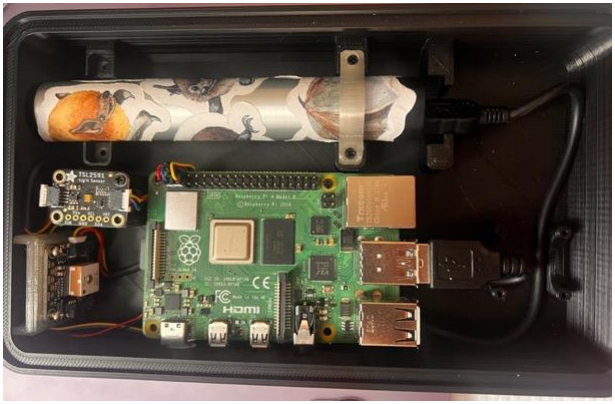
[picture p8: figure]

Plate 5: Final EchoPiBox 2.0 (EPB) Hardware Assembly (Smoldareva, 2023)

More detailed hardware and software instructions of the set up can be found here: https://github.com/Rita888/EchoPiBox-2.0/blob/main/EchoPibox%202.0%20-%20Built%20Your%20Own%20Instructions.pdf (https://github.com/Rita888/EchoPiBox-2.0/blob/main/EchoPibox%202.0%20-%20Built%20Your%20Own%20Instructions.pdf)

CLASSIFY – IDENTIFICATION AND TESTING ACCURACY

To classify bat social calls, open source BatDetect2 (Macaodha, 2023¹ ) model was used to
build up on to produce Acoupi software²
. The Acoupi software utilises the code used to run the BatDetect2 algorithm.

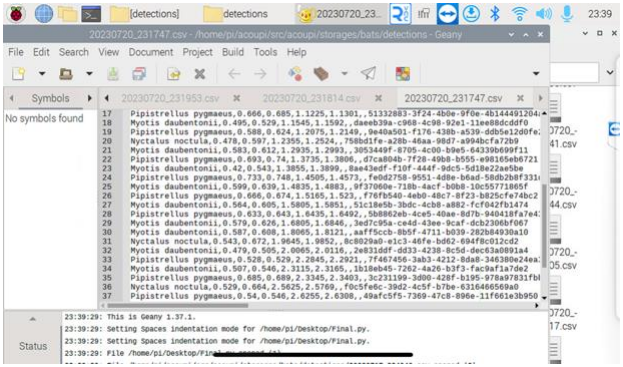
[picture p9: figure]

Raw data produced by Acoupi software in Raspberry Pi.

For this project, series of sites were selected to include habitat complexity that would allow different bat species to be present to test the accuracy of detecting as many of UK bat species at possible. The Bat Conservation Trust (BCT, 2023) provides comprehensive guidelines for conducting bat surveys, ranging from preliminary assessment, emergence/re-entry, transect and roost surveys.

Due to personal experience of undertaking diverse bat surveys over eight years, it was possible to select sites in England and Wales with known presence of bats. Five sites were of diverse habitats and surrounding landscapes as described later in this chapter. The surveyor holds Natural England Level 1 Bat Licence therefore permitted to use artificial light to identify bat species.

1 https://github.com/macaodha/batdetect2

2 https://github.com/audevuilli/acoupi (private repository as still in development)

The nocturnal bat surveys commenced 20 minutes prior to sunset and completed around 90 to 120 minutes after the sunset. In conjunction to EchoPiBox 2.0, Echo Meter Touch (EMT) Pro for iOS from used to then compare the species recorded. The recordings were later analysed using Wildlife Acoustics Software to verify bat calls recorded on EMT.

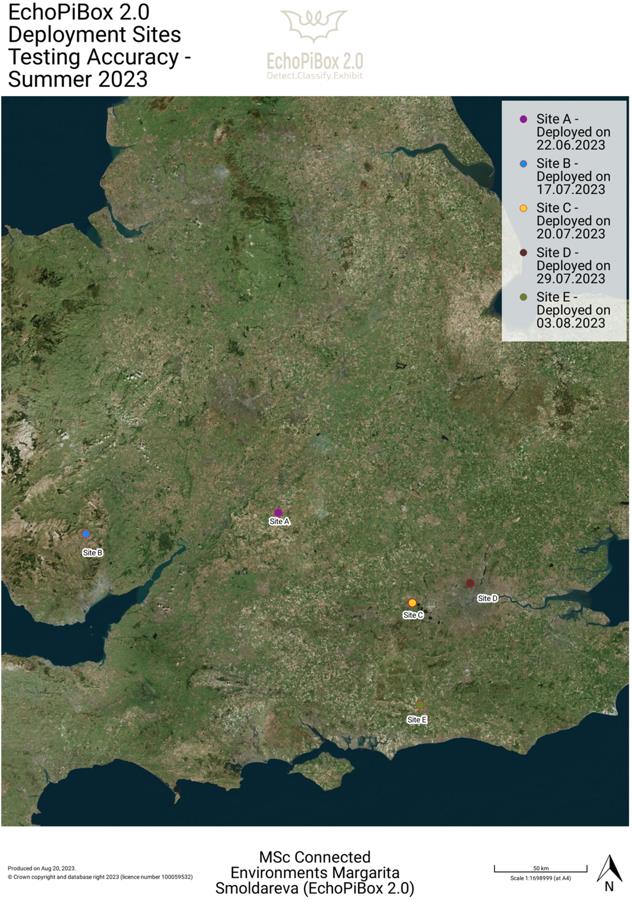
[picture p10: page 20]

### DEPLOYMENT RESULTS

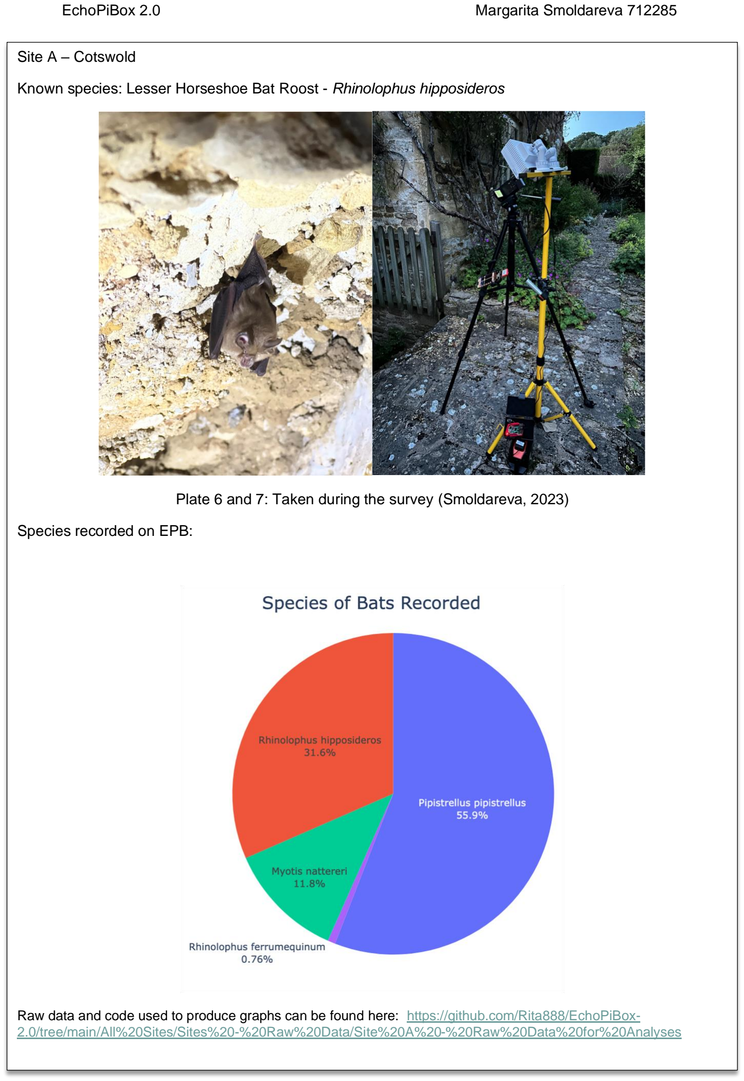
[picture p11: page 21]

Site A – Cotswold

Known species: Lesser Horseshoe Bat Roost - Rhinolophus hipposideros

Plate 6 and 7: Taken during the survey (Smoldareva, 2023)

Species recorded on EPB:

Raw data and code used to produce graphs can be found here: https://github.com/Rita888/EchoPiBox-2.0/tree/main/All%20Sites/Sites%20-%20Raw%20Data/Site%20A%20-%20Raw%20Data%20for%20Analyses (https://github.com/Rita888/EchoPiBox-2.0/tree/main/All%20Sites/Sites%20-%20Raw%20Data/Site%20A%20-%20Raw%20Data%20for%20Analyses)

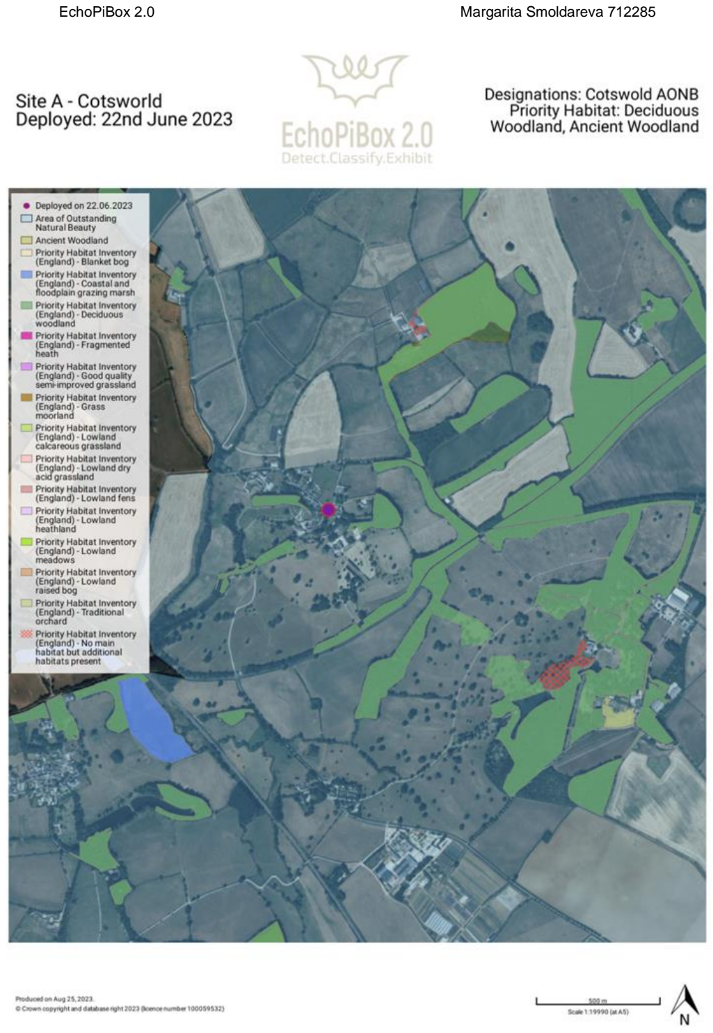
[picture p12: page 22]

Site B – South Wales

Known species: Lesser Horseshoe Bat - Rhinolophus hipposideros, Myotis sp. inside the cave.

Plate 8 and 9: Taken during the survey (Smoldareva, 2023)

Species recorded on EPB:

Raw data and code used to produce graphs can be found here: https://github.com/Rita888/EchoPiBox-2.0/tree/main/All%20Sites/Sites%20-%20Raw%20Data/Site%20B%20-%20Raw%20Data%20for%20Analyses (https://github.com/Rita888/EchoPiBox-2.0/tree/main/All%20Sites/Sites%20-%20Raw%20Data/Site%20B%20-%20Raw%20Data%20for%20Analyses)

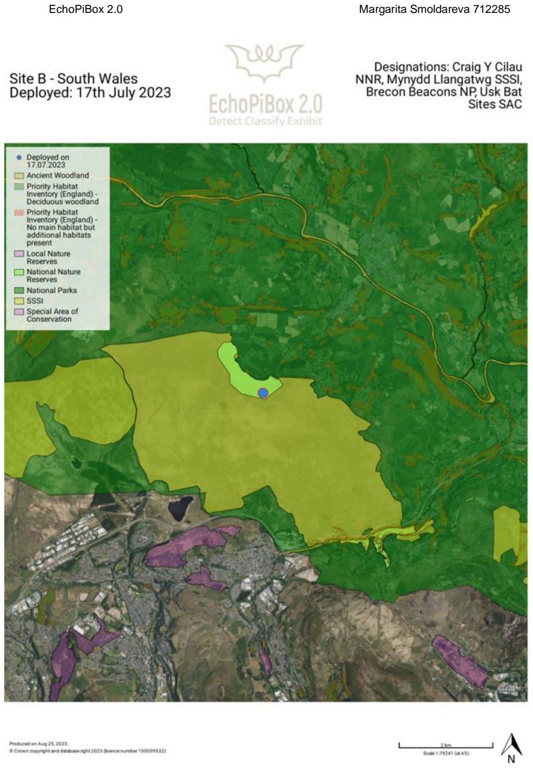
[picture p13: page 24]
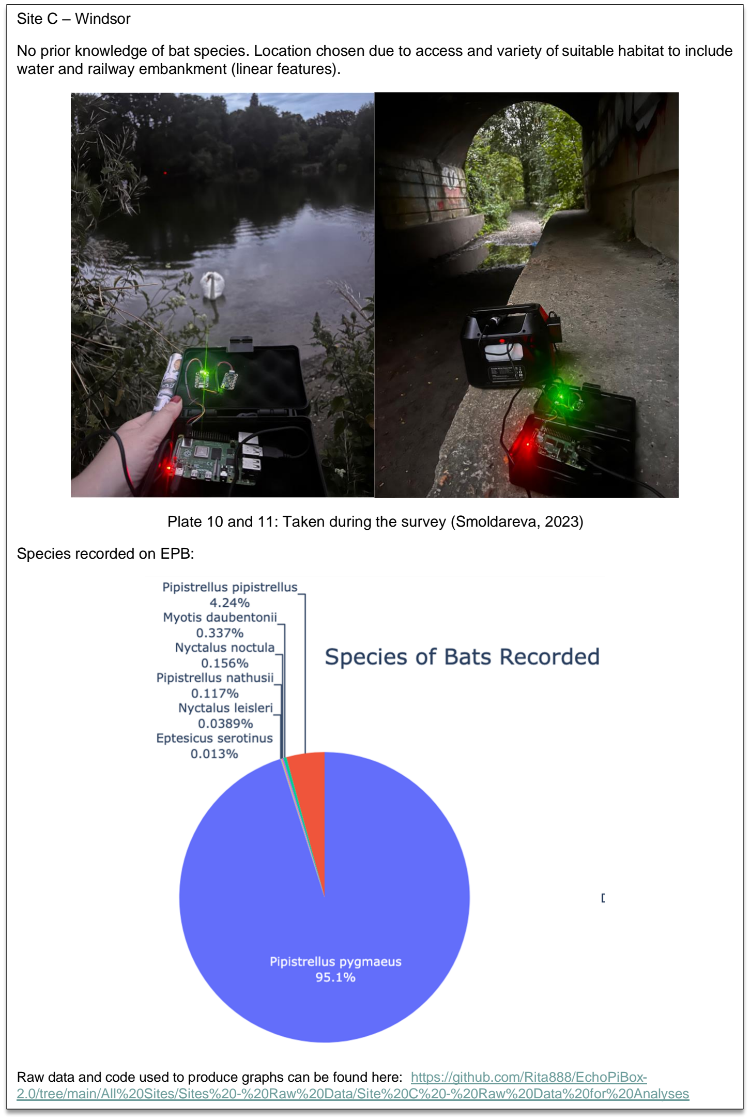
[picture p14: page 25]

Site C – Windsor

No prior knowledge of bat species. Location chosen due to access and variety of suitable habitat to include water and railway embankment (linear features).

Plate 10 and 11: Taken during the survey (Smoldareva, 2023)

Species recorded on EPB:

Raw data and code used to produce graphs can be found here: https://github.com/Rita888/EchoPiBox-2.0/tree/main/All%20Sites/Sites%20-%20Raw%20Data/Site%20C%20-%20Raw%20Data%20for%20Analyses (https://github.com/Rita888/EchoPiBox-2.0/tree/main/All%20Sites/Sites%20-%20Raw%20Data/Site%20C%20-%20Raw%20Data%20for%20Analyses)

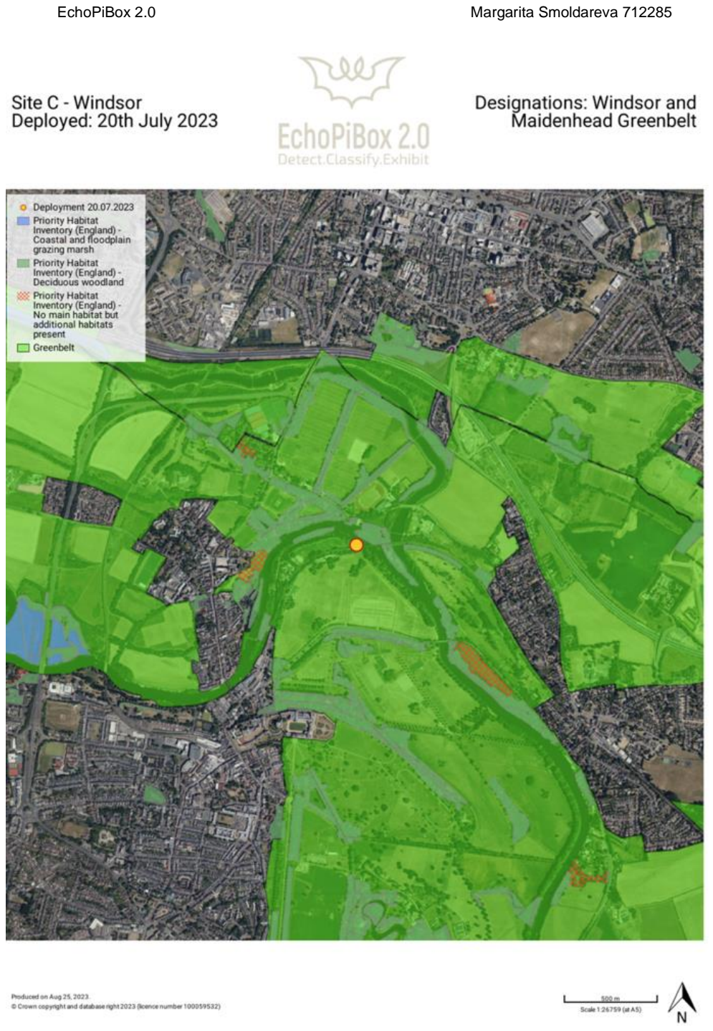
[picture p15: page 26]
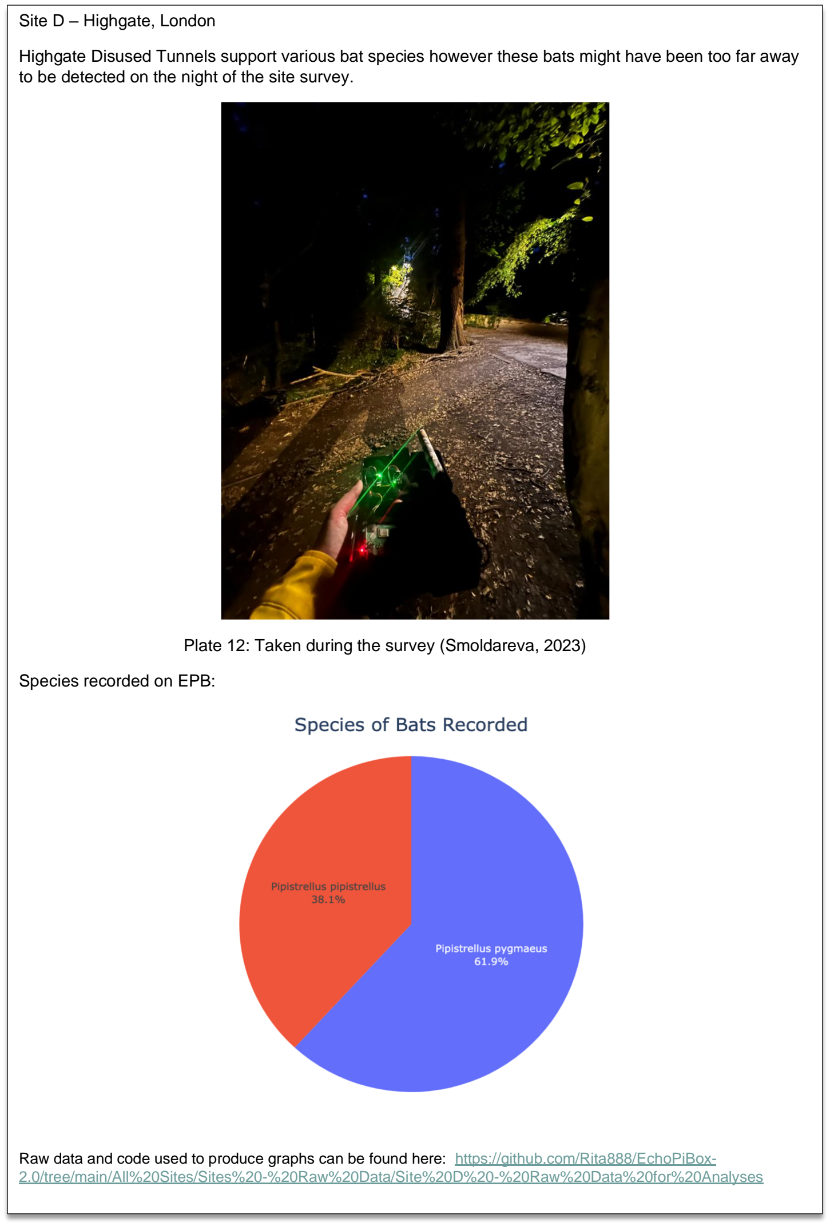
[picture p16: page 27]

Site D – Highgate, London

Highgate Disused Tunnels support various bat species however these bats might have been too far away to be detected on the night of the site survey.

Plate 12: Taken during the survey (Smoldareva, 2023)

Species recorded on EPB:

Raw data and code used to produce graphs can be found here: https://github.com/Rita888/EchoPiBox-2.0/tree/main/All%20Sites/Sites%20-%20Raw%20Data/Site%20D%20-%20Raw%20Data%20for%20Analyses (https://github.com/Rita888/EchoPiBox-2.0/tree/main/All%20Sites/Sites%20-%20Raw%20Data/Site%20D%20-%20Raw%20Data%20for%20Analyses)

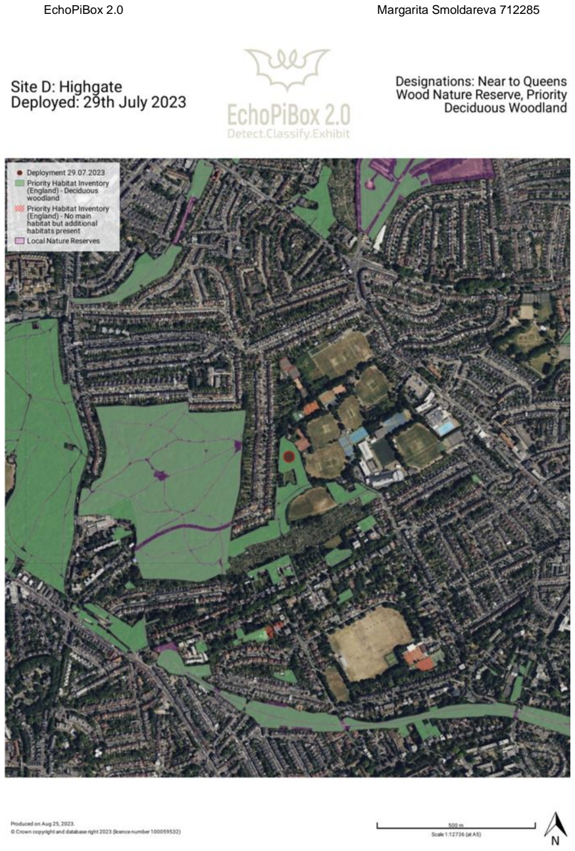
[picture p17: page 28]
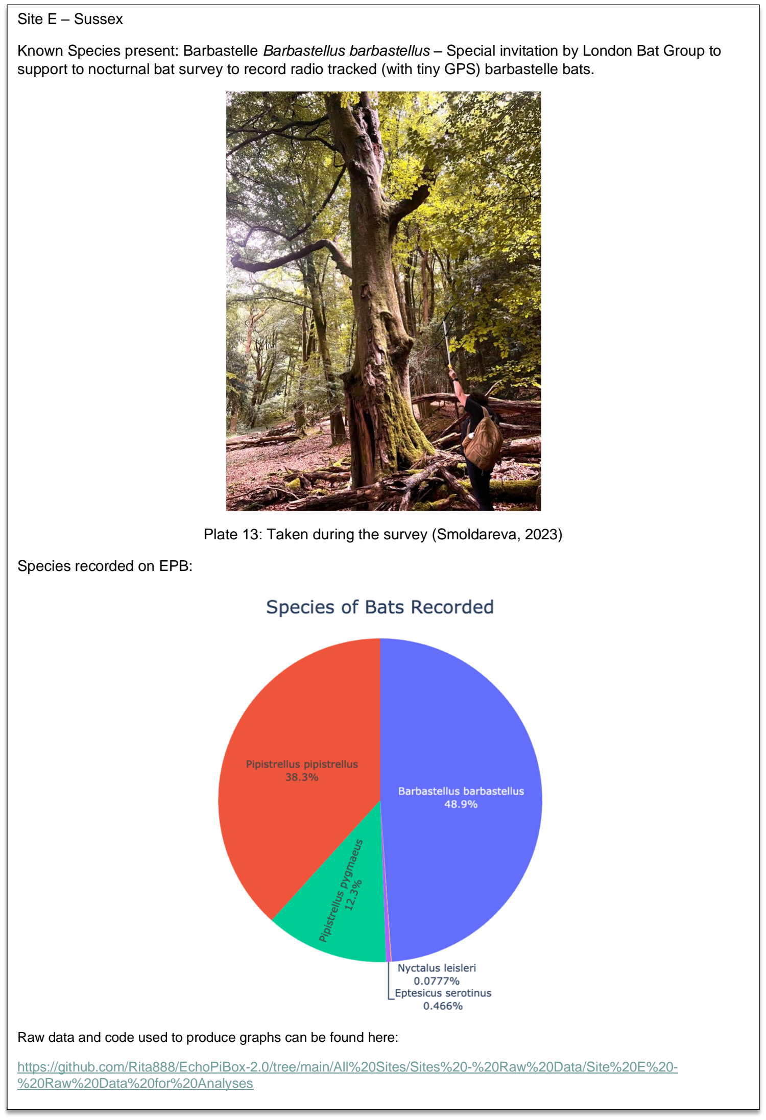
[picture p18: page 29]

Site E – Sussex

Known Species present: Barbastelle Barbastellus barbastellus – Special invitation by London Bat Group to support to nocturnal bat survey to record radio tracked (with tiny GPS) barbastelle bats.

Plate 13: Taken during the survey (Smoldareva, 2023)

Species recorded on EPB:

Raw data and code used to produce graphs can be found here:

https://github.com/Rita888/EchoPiBox-2.0/tree/main/All%20Sites/Sites%20-%20Raw%20Data/Site%20E%20-%20Raw%20Data%20for%20Analyses (https://github.com/Rita888/EchoPiBox-2.0/tree/main/All%20Sites/Sites%20-%20Raw%20Data/Site%20E%20-%20Raw%20Data%20for%20Analyses)

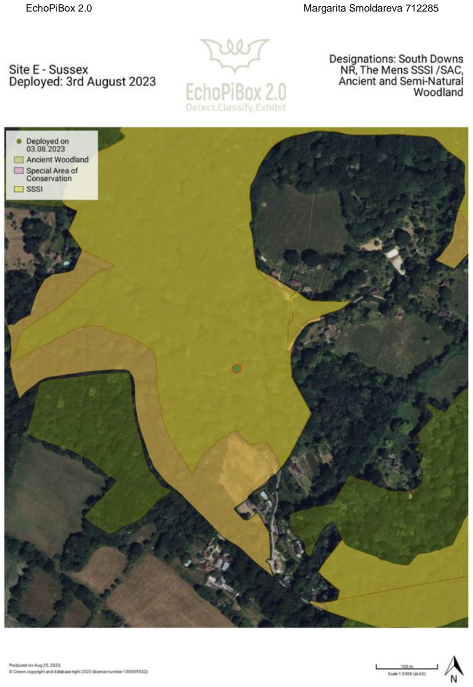
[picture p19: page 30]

Raw data and code used to produce graphs can be found here:

https://github.com/Rita888/EchoPiBox-2.0/blob/main/All%20Sites/output_combined.csv

https://github.com/Rita888/EchoPiBox-2.0/blob/main/All%20Sites/compile.py

EXHIBIT – DISPLAY REAL TIME DATA ON FLUTTER APP

Once the data collected using EMT was analysed using Kaleidoscope Viewer for Bat Analysis (Wildlife Acoustics, 2023) it then compared to the data collected using EchoPiBox
2.0. The accuracy of the Acoupi detection was set to 60% therefore any bat calls with less than 59% would not be displayed on the app.

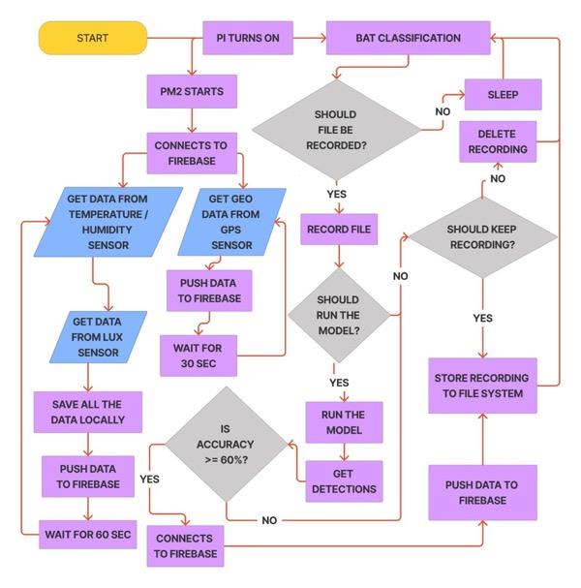
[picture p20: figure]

Flow chart 2: Overall Detection, Classification and Display Flow Chart

More details are here: https://github.com/Rita888/EchoPiBox-2.0/blob/main/EchoPibox%202.0%20-%20Built%20Your%20Own%20Instructions.pdf (https://github.com/Rita888/EchoPiBox-2.0/blob/main/EchoPibox%202.0%20-%20Built%20Your%20Own%20Instructions.pdf)

and here https://github.com/Rita888/EchoPiBox-2.0-app

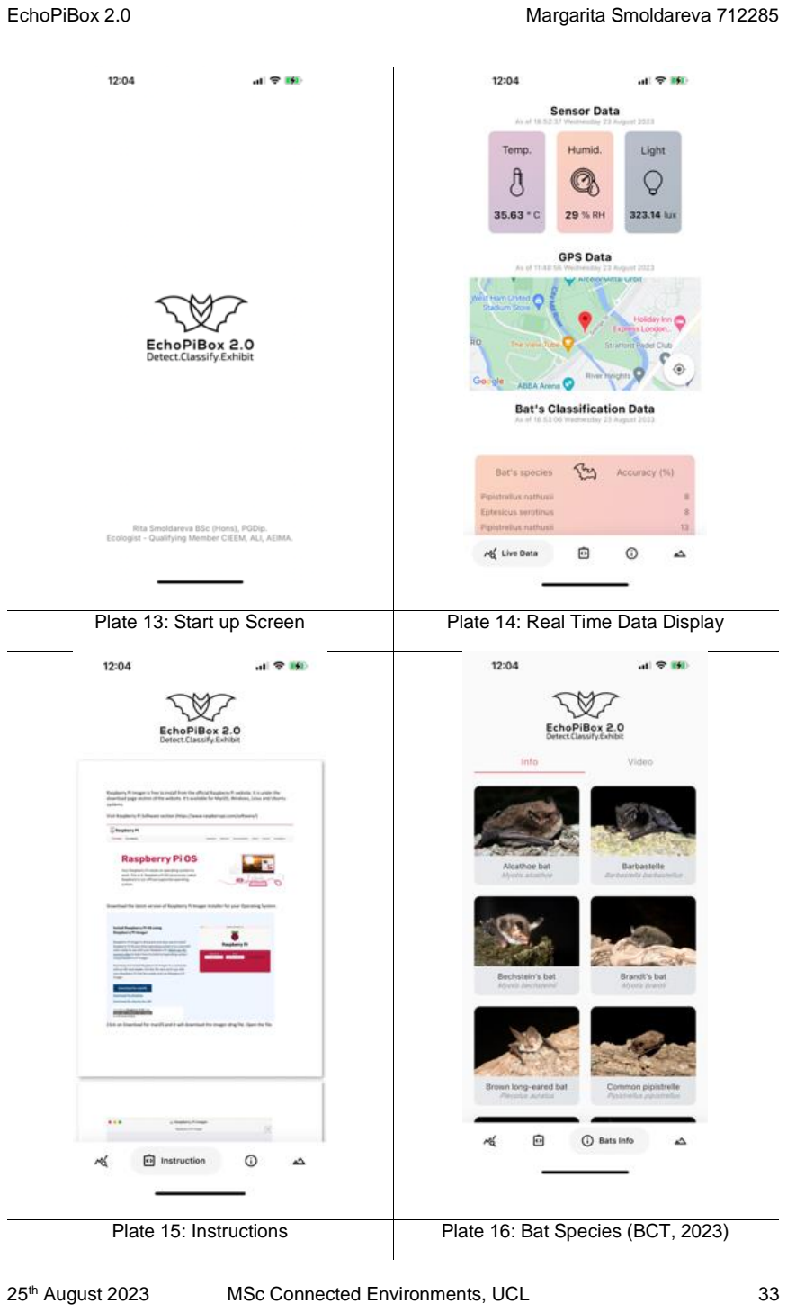
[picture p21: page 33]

Plate 13: Start up Screen | Plate 14: Real Time Data Display
Plate 15: Instructions | Plate 16: Bat Species (BCT, 2023)

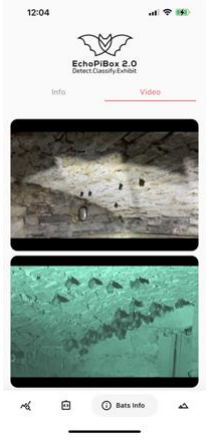
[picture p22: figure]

Plate 17: Videos within the app (Smoldareva, 2023)

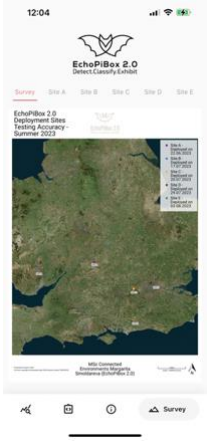
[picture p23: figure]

Plate 18: Deployment Sites Information

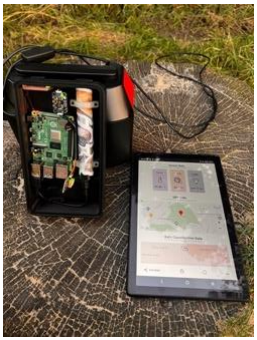
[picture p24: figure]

Plate 19: Final test before the exhibition (Smoldareva, 2023)

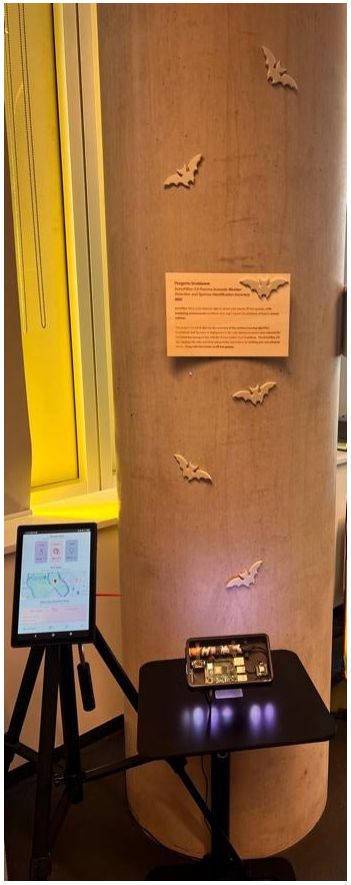
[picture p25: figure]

Plate 20: Inside Urban Room exhibition

### DISCUSSION AND FURTHER RECOMMENDATIONS

BUILDING THE EPB– The aim of this study was to include the hardware that will be used to correctly identify bat species while deployed in the wild. The ultramic and the sensors did not present any challenges during the deployment. The power source was not discussed in this project as the main aims were to build a working bat detector, test the accuracy of the BatDetect2 model and display real time data using flutter app. As this device can be used as a handheld detector as well as a static detector, therefore deployed over series of nights, weeks, months or be permanently installed on a lamppost. For this study portable DC/AC Power Bank with 99WH capacity was used as the surveys were lasting over two hours at each of the time. If these are to be used as static detector, different power source should be used to accommodate the power consumption of the Raspberry Pi.

It must be also noted that the sensors were not calibrated and not tested during this study therefore further testing is recommended. Although, the real time data was displayed on the app, the accuracy of data particularly was lux, temp/humidity sensors were not tested due to lack of time. The GPS location was out by 25 to 50m which is suitable for this study however if more precise location is needed, use of another sensor is recommended.

Also to be noted that due to 11-12 hours deployment time, the environmental data recorded was insufficient to allow any analysis of these parameters to determine accuracy of bat species such as the light sensitive bat species (e.g. Brown Long-eared bat and Myotis sp.) Further assessment would allow lux sensor to determine likelihood of bat species present within the locality.

SETTING UP THE EPB– The software element was the most challenging in this study and about 70 per cent of the time spent on the project was to set up the Raspberry pi and provide the code for the sensors due to non-engineering background. Hence the detailed guid was produced to allow fellow ecologists with non-engineering background to navigate through EchoPiBox 2.0 set up.

BATDETECT2/ACOUPI were easy to install once the Raspberry Pi was set up. Several deployments were undertaken prior to conducting surveys away from home. The accuracy was tested and concluded that any detections above 60% will be displayed on the real time data stream and anything less than 59% will be discarded. It is recommended that further deployments and tests are carried out to conclude on the accuracy percentage as just over ten hours of recordings cannot be sufficient to conclude on the accuracy. It is also recommended to deploy in different locations to capture all 17 UK species as only 11 species were classified during this study.

The raw data shown that 14 species were recorded on one night of deployment however once the accuracy was changed to 60% this number dropped to 6 species. The species might be occupying that specific location however due to only two-hour deployment; these bat species might have been too far away to be detected accurately.

CONNECTIVITY – During the deployment, to test if the EPB is switched on, personal smart phone hotspot and TeamViewer App was used. Once the Flutter App was build, Alcatel 8094T Android tablet was used for hotspot connection. The device can be used in the wild without connectivity however there is a risk that the automated (PM2) is not running therefore not recording the data. The app allows to test if the device is operating by displaying the real time data however another way of connectivity must be explored to allow other sources of connection such as Long Range Wide Area Network (LoRaWAN). This will enable long range communication with low power consumption, allowing appliactions requires remote and battery-operated devices to transmit data over relatively long distances.

THERMAL CONSTRAINTS – Once the device was inside its 3D printed box, the temperature emitted from the Raspberry Pi started to influence the sensor. For further design improvements, the temperature/humidity sensor should be placed outside the device box to avoid the false data reading.

STORAGE – For this project 64GB SD card was used at the initial stage and by the second night of deployment, it was noted that more storage is needed. The SD was backed up and cloned using ApplePiBaker Software (PiBaker, 2023) on varies occasions to allow 256GB SD to be the final operation SD card installed within the Raspberry Pi 4.

RAM – The Raspberry Pi 4 which was used for this study had 8GB which is lower than the traditional desktop or laptop computers. Although, the real time data was displayed on the app, there is a slight delay and at the time of the write is was inconclusive if this issue was due to RAM or Firebase/iCloud limitations.

BETTER IOT – To make this device more sustainable, it is advised to use the assessment tool provided by the Better IOT. This tool was developed to address some of the pressing issue in the early stages of development to include: “privacy, openness, interoperability, lifecycle, permissions, transparency, data governance and security”. (BetterIOT, 2023).

### CONCLUSION

This study had three aims and objectives: Detect, Classify and Exhibit, as stated at the start of this document. The physical device has all the hardware components needed to start recording bat calls as well as additional sensors that could impact on presence of bats such as temperature, artificial light and the location. To classify the bat calls collected, open-source machine learning Acoupi software (stemmed from BatDetect2 model) was installed on Raspberry Pi.

The device was installed over 10 hours, approximately 2 hours at each of five different locations in England and Wales to detect as many bat species as possible. In total 11 species were recorded during deployment and the accuracy of open-source model was concluded to be precise. Due to Ultramic is very sensitive and many misclassifications were recorded and the accuracy of the detection was then coded to 60% which reduced the species recorded from 14 to 11.

The data collected was then sent to iCloud (Firebase) which then allowed the real time data to be displayed on the EchoPibox 2.0 Flutter App. There was a slight delay of several seconds in displaying the data depending on its connectivity to WiFi or Mobile Hotspot.

Overall, the study was successful however the report highlighted several improvements and recommendations in the discussion section to include power supply, calibrating the sensors, connecting to stable data transmitting network, redesigning the enclosure box to be more robust and complaint with International Protection Rating (IPR). Lastly, it is also advisable to use Better IOT assessment tool to allow the device to be in line with sustainability.

REFERENCES

Applepi-Baker v2 for Raspberry Pi. Tweaking4All. (https://www.tweaking4all.com/software/macosx-software/applepi-baker-v2/ (https://www.tweaking4all.com/software/macosx-software/applepi-baker-v2/) Accessed on 20th July 2023

Bat Conservation Trust. Guidance for professionals. (https://www.bats.org.uk/resources/guidance-for-professionals) (https://www.bats.org.uk/resources/guidance-for-professionals) Accessed on 10th May 2023

Better IOT. Making Good Design Actionable. (https://betteriot.wordpress.com) accessed on 25th August 2023

Buchler, E. R. (1975). Food transit time in Myotis lucifugus Chiroptera: Vespertilionidae. Journal of Mammalogy, 56(1), 252-255.

Clement, M.J., Murray, K.L., Solick, D.I. and Gruver, J.C., 2014. The effect of call libraries and acoustic filters on the identification of bat echolocation. Ecology and evolution, 4(17), pp.3482-3493.

Cravens, Z.M. and Boyles, J.G., 2019. Illuminating the physiological implications of artificial light on an insectivorous bat community. Oecologia, 189, pp.69-77.

Darras, K.F.A., Yusti, E., Huang, J.C.C., Zemp, D.C., Kartono, A.P. and Wanger, T.C., 2021. Bat point counts: A novel sampling method shines light on flying bat communities. Ecology and Evolution, 11(23), pp.17179-17190.

Entwhistle, A.C., Harris, S., Hutson, A.M., Walsh, A., Gibson, S.D., Hepburn, I. and Johnston, J., 2001. Habitat management for bats-a guide for land managers, land owners and their advisors.

Fritsch, G. and Bruckner, A., 2014. Operator bias in software‐aided bat call identification. Ecology and evolution, 4(13), pp.2703-2713.

Gallacher, S., Wilson, D., Fairbrass, A., Turmukhambetov, D., Firman, M., Kreitmayer, S., Mac Aodha, O., Brostow, G. and Jones, K., 2021. Shazam for bats: Internet of Things for continuous real‐time biodiversity monitoring. IET Smart Cities, 3(3), pp.171-183.

Hill, D. A., & Greenaway, F. (2008). Conservation of bats in British woodlands. British Wildlife, 19(3), 161.

Horsey, J. (2023, July 17). Listen to bats using the raspberry Pi Pico bat detector. Geeky Gadgets. https://www.geeky-gadgets.com/raspberry-pi-bat-detector-17-07-2023/

Jolles, J.W., 2021. Broad‐scale applications of the Raspberry Pi: A review and guide for biologists. Methods in Ecology and Evolution, 12(9), pp.1562-1579.

Kasso, M., & Balakrishnan, M. (2013). Ecological and economic importance of bats (Order Chiroptera). Isrn Biodiversity, 2013, 1-9.

Laforge, A., Pauwels, J., Faure, B., Bas, Y., Kerbiriou, C., Fonderflick, J. and Besnard, A., 2019. Reducing light pollution improves connectivity for bats in urban landscapes. Landscape Ecology, 34, pp.793-809.

Mac Aodha, O., Gibb, R., Barlow, K.E., Browning, E., Firman, M., Freeman, R., Harder, B., Kinsey, L., Mead, G.R., Newson, S.E. and Pandourski, I., 2018. Bat detective—Deep learning tools for bat acoustic signal detection. PLoS computational biology, 14(3), p.e1005995.

Mac Aodha, O., Martinez Balvanera, S., Damstra, E., Cooke, M., Eichinski, P., Browning, E., Barataud, M., Boughey, K., Coles, R., Giacomini, G. and Mac Swiney G, M.C., 2022. Towards a General Approach for Bat Echolocation Detection and Classification. bioRxiv, pp.2022-12.

Mendes, E.S., Fonseca, C., Marques, S.F., Maia, D. and Ramos Pereira, M.J., 2017. Bat richness and activity in heterogeneous landscapes: guild-specific and scale-dependent?. Landscape ecology, 32, pp.295-311.

Nationwide Ecology Supplies. Bat Detectors. https://www.wildcare.co.uk/media/amasty/amfile/attach/r7DGJpG7YFh6ydqaKHuKLH1QFbJUxTKa.p df (https://www.wildcare.co.uk/media/amasty/amfile/attach/r7DGJpG7YFh6ydqaKHuKLH1QFbJUxTKa.pdf) (accessed on 11th August 2023)

Raspberry Pi bat project. (n.d.). Raspberry Pi Bat Projekt. https://www.bat-pi.eu/EN/index-EN.html

Ruiz, A.T., Jung, K., Tschapka, M., Schwenker, F. and Palm, G., 2017. Automated identification method for detection and classification of neotropical bats.

Simmons, J.A. and Gaudette, J.E., 2012. Biosonar echo processing by frequency-modulated bats. IET Radar, Sonar & Navigation, 6(6), pp.556-565.

Skowronski, M.D. and Fenton, M.B., 2008. Model-based automated detection of echolocation calls using the link detector. The Journal of the Acoustical Society of America, 124(1), pp.328-336.

Suga, N., 1990. Biosonar and neural computation in bats. Scientific American, 262(6), pp.60-71.

Voigt, C.C., Scholl, J.M., Bauer, J., Teige, T., Yovel, Y., Kramer-Schadt, S. and Gras, P., 2020. Movement responses of common noctule bats to the illuminated urban landscape. Landscape Ecology, 35, pp.189-201.

Walters, C.L., Collen, A., Lucas, T., Mroz, K., Sayer, C.A. and Jones, K.E., 2013. Challenges of using bioacoustics to globally monitor bats. Bat evolution, ecology, and conservation, pp.479-499.

Wang, J. and Bu, Y., 2022. Internet of Things‐based smart insect monitoring system using a deep neural network. IET Networks, 11(6), pp.245-256.

Whittaker, A. (2020, October 16). Ultrasonically detect bats with raspberry Pi. Raspberry Pi. https://www.raspberrypi.com/news/ultrasonically-detect-bats-with-raspberry-pi/

Whytock, R.C. and Christie, J., 2017. Solo: an open source, customizable and inexpensive audio recorder for bioacoustic research. Methods in Ecology and Evolution, 8(3), pp.308-312.

Zeale, M.R., Stone, E.L., Zeale, E., Browne, W.J., Harris, S. and Jones, G., 2018. Experimentally manipulating light spectra reveals the importance of dark corridors for commuting bats. Global Change Biology, 24(12), pp.5909-5918.

References for Codes (Excluding BatDecect2/Acoupi – noted as footnotes on page 18)

Temperature/Humidity Sensor: https://github.com/adafruit/Adafruit_CircuitPython_SHT4x

Lux Sensor: https://github.com/adafruit/Adafruit_CircuitPython_TSL2591

GPS Sensor: https://github.com/adafruit/Adafruit_CircuitPython_GPS

Automated Process: https://github.com/Unitech/pm2

Firebase API for Flutter App: https://github.com/thisbejim/Pyrebase

The following codes were used for bat call data analysis recorded only by EchoPiBox 2.0

https://github.com/pandas-dev/pandas

https://github.com/numpy/numpy

https://github.com/plotly/plotly.py

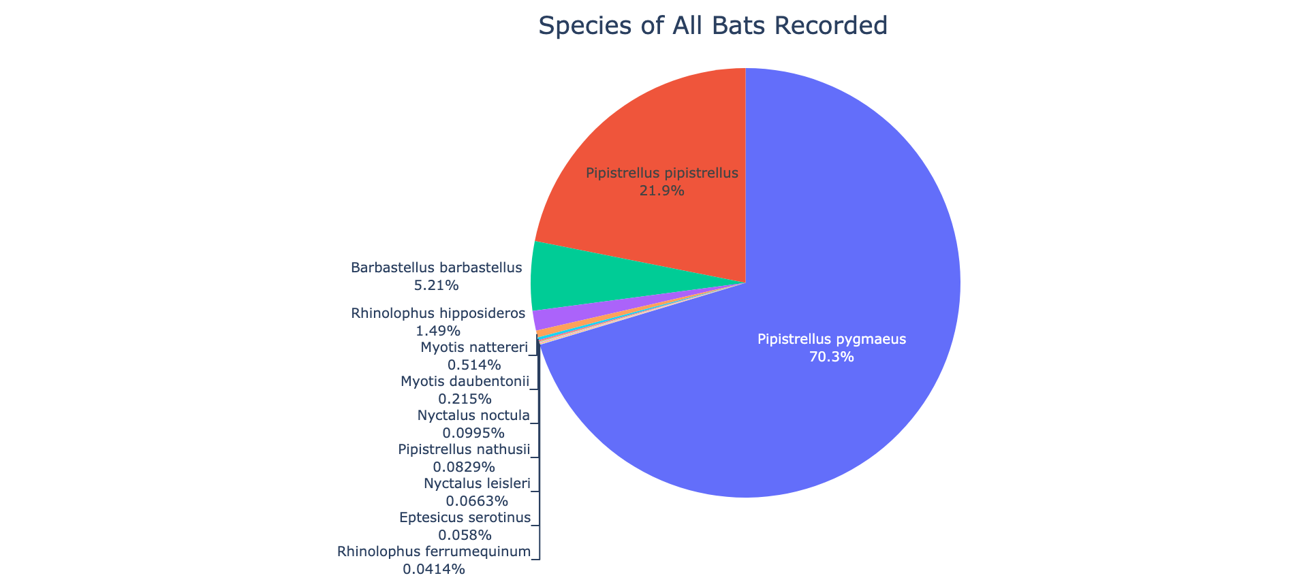
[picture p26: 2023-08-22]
All Sites.png

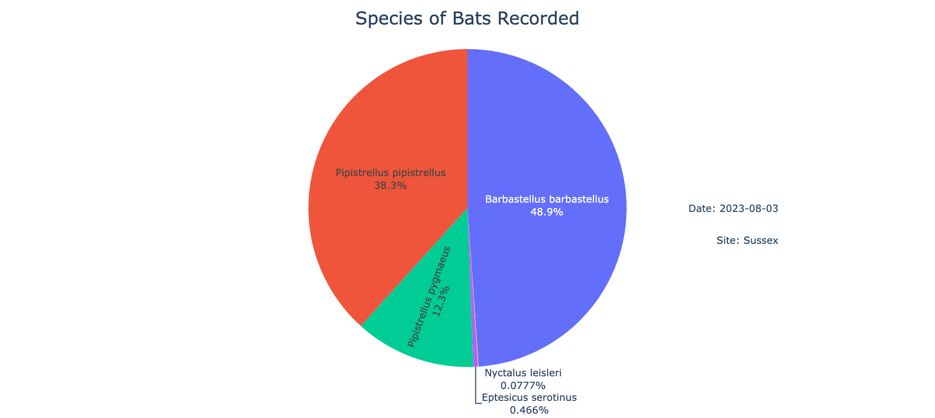
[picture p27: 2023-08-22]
Graphs/Site E.png

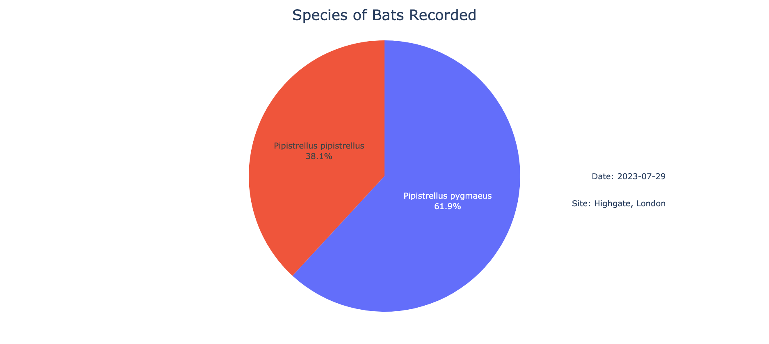
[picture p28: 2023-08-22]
Graphs/Site D.png

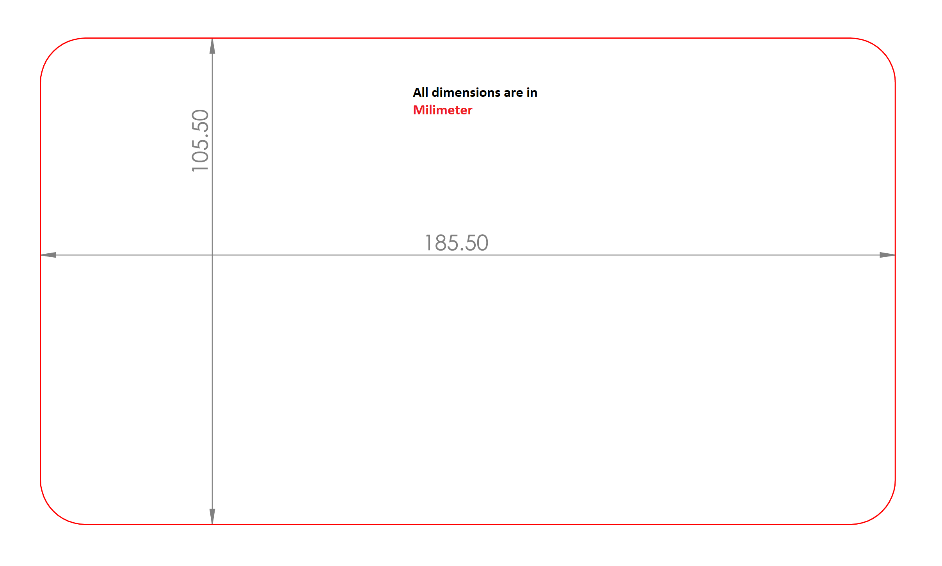
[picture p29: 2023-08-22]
Rita Enclosure V1/Laser Cutting Files/Dimensions.png

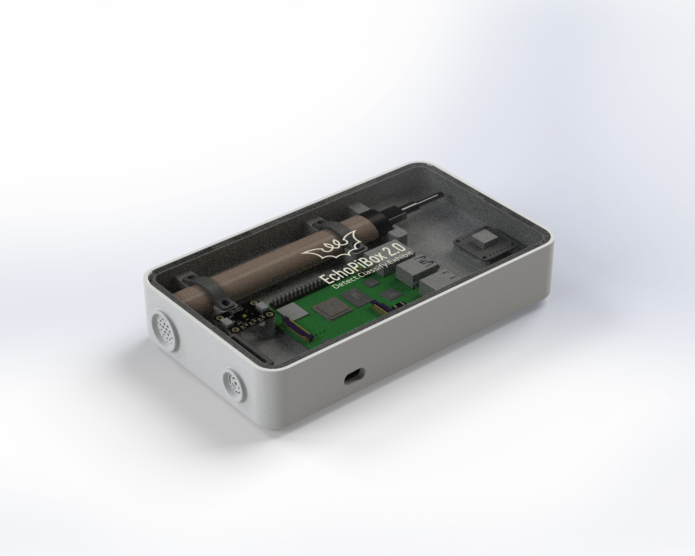
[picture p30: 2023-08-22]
Rita Enclosure V1/Render (3).png

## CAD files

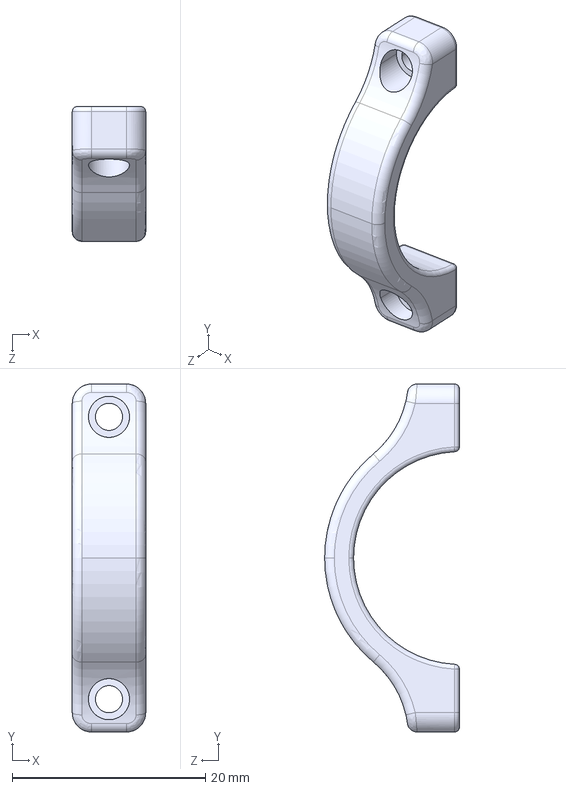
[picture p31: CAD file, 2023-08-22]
Rita Enclosure V1/3D Printing Files/STEP Files/Clamp.STEP
7.60 x 36.0 x 13.9 mm

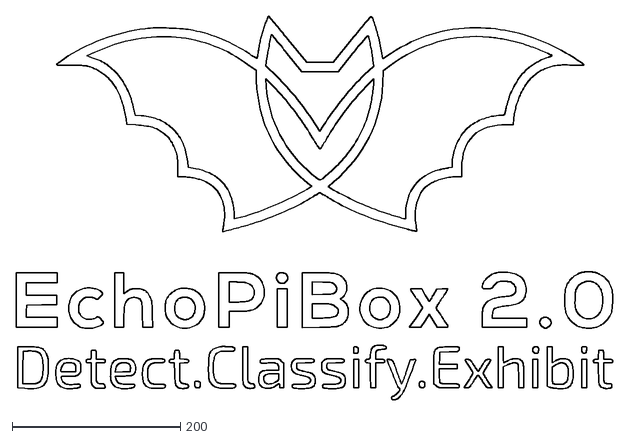
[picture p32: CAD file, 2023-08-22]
Rita Enclosure V1/Laser Cutting Files/Logo_Acrylic-Glass-Lid.dxf
709.0 x 455.8

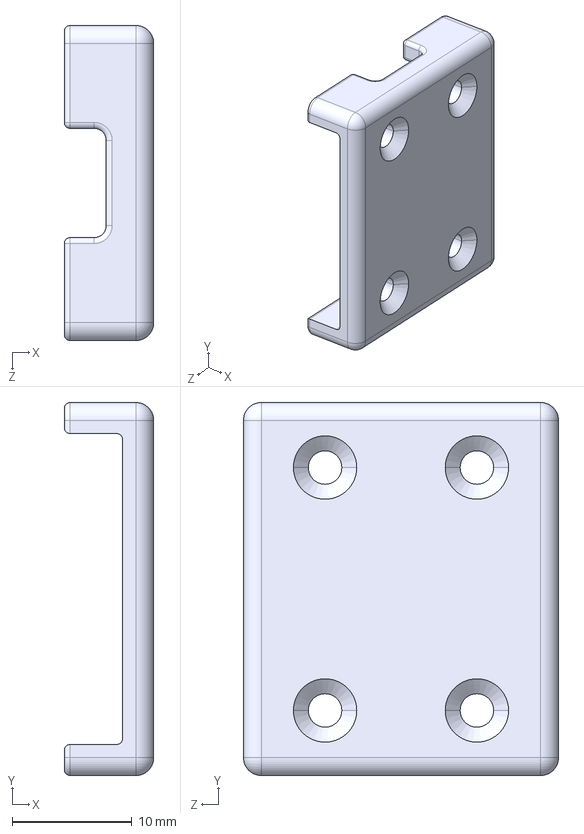
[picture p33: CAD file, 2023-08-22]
Rita Enclosure V1/3D Printing Files/STEP Files/Temperature Wall.STEP
7.49 x 31.2 x 26.4 mm

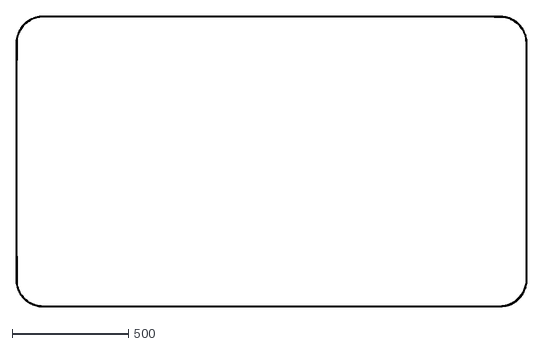
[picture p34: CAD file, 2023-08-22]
Rita Enclosure V1/Laser Cutting Files/Acrylic-Glass-Lid.dxf
2194.0 x 1249.1

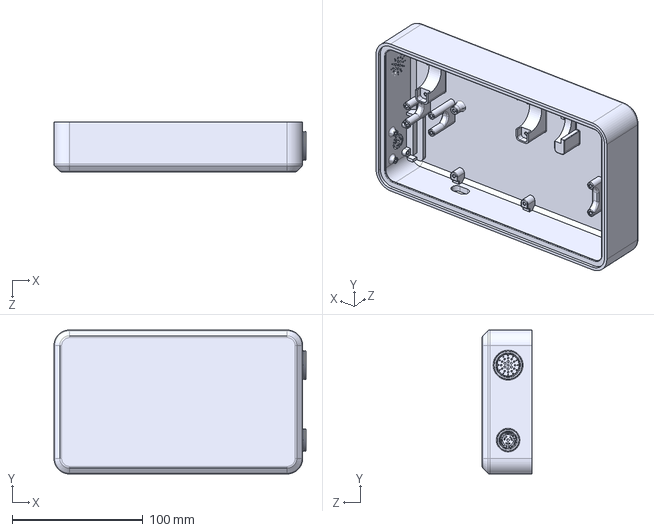
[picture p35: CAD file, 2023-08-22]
Rita Enclosure V1/3D Printing Files/STEP Files/Base.STEP
192.5 x 110.0 x 38.0 mm

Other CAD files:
Rita Enclosure V1/3D Printing Files/STL Files/Base.STL
Rita Enclosure V1/3D Printing Files/STL Files/Clamp.STL
Rita Enclosure V1/3D Printing Files/STL Files/Temperature Wall.STL

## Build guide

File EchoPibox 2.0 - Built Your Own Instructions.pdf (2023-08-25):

# BUILD YOUR OWN

## Detailed Instructions (for IOS users only)

## Margarita Smoldareva

University College London, MSc Connected Environments, 2023

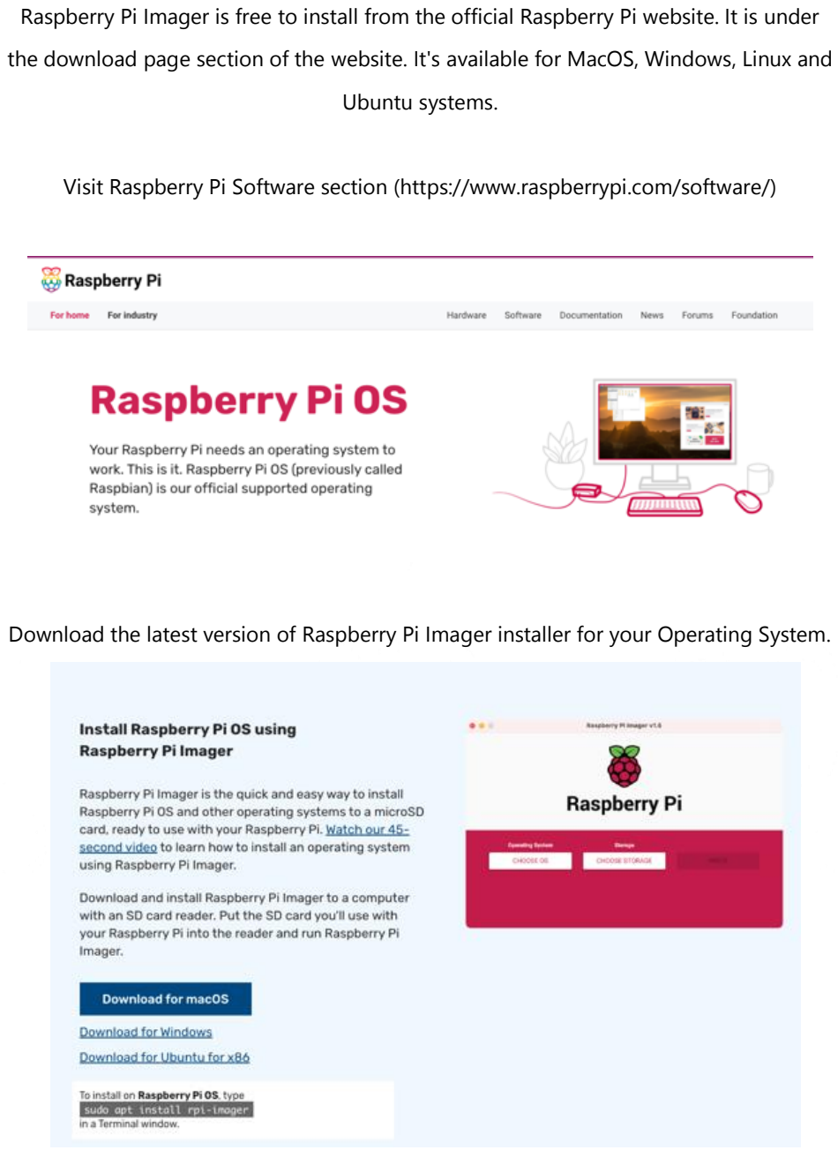
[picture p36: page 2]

Raspberry Pi Imager is free to install from the official Raspberry Pi website. It is under

the download page section of the website. It's available for MacOS, Windows, Linux and

Ubuntu systems.

Visit Raspberry Pi Software section (https://www.raspberrypi.com/software/)

Download the latest version of Raspberry Pi Imager installer for your Operating System.

Click on Download for macOS and it will download the imager.dmg file. Open the file.

Once the file is open simply drag and drop Raspberry Pi Imager into the Applications

folder and the program should be installed.

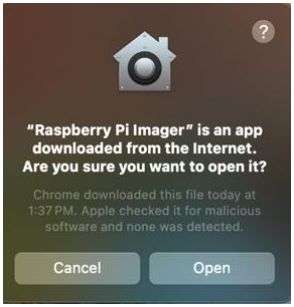
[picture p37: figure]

Now open Raspberry Pi Imager from the launchpad and the above prompt will appear.

Click on Open. The program should open.

Now click on CHOOSE OS.

Operating System pop up will open. Click on Raspberry Pi OS (other). This project needs

64-bit OS for this development.

Scroll a bit down and choose Raspberry Pi OS (64-bit). Keep an eye on the size, this

should be 0.8 GB as we need Desktop version of Debian Bullseye.

It will take you back once you select the OS. Insert the SD card into the mac. Now click

on CHOOSE STORAGE.

Select the SD card.

We can use Raspberry Pi Imager to setup a raspberry pi in the headless mode without

the need for additional peripherals such as monitor, keyboard and mouse. By

configuring our Wi-fi credentials and locale settings into the OS we can use this imaging

tool to write the OS onto the SD card. So, we click on the setting logo.

A prompt would ask saying Would you like to prefill the Wi-Fi password from the

system keychain? For easier access we can select Yes.

It will ask for system credentials. Please provide the credentials and click on Allow.

You can select Image customization options to “to always use”. Select Enable SSH.

Then scroll down a bit.

The set Username as “pi” and password as “raspberry”. And also provide your Wi-Fi

credentials.

Then scroll again.

and select on set locale settings and choose your desired Time zone and Keyboard

layout. Click on SAVE.

It will take you back to the home screen. Now simply press WRITE button. The process

will start.

Click on YES.

Please verify either using fingerprint or password and the process will start writing the

OS into the SD card.

Once the writing process is complete it will prompt a message with Write Successful

message. Click on CONTINUE. Remove the SD card from the laptop.

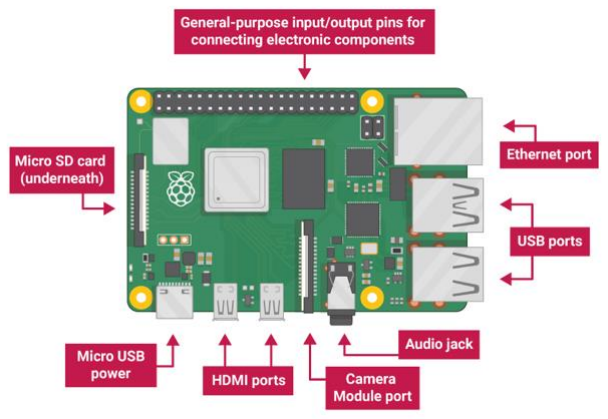
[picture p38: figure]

Insert the SD card in the raspberry pi. Connect the Micro USB power using raspberry pi 4

official power supply. The red and green status LED on the side of the Micro USB power

will start to blink.

Now once the pi boots up it will connect to the Wi-Fi; we provided credentials in the

setup section. In order to connect to the Pi, we need to know the IP address of the

raspberry pi. For that purpose, we can use a software called angry IP scanner. It's

available for MacOS, Windows, Linux and Ubuntu systems.

Visit (https://angryip.org/download/#mac)

Select the mac type and download the file. Once the file is downloaded.

MacOS will prompt with this message. You will have to Cancel this. Developer mode has

to be enabled in the system. After that go to mac’s Settings, then Privacy and Security

then scroll until you see this.

Click on Open Anyway. It will prompt for password provide the password.

Click on Open. The application will open. Click on Start.

Once the process is complete. Close the prompt. Select anyone of the IP address. Press

CMD+H until you see raspberrypi.local on the host name. Sometimes raspberry pi will not be able to connect to the Wi-Fi. In that case an ethernet cable can be connected

directly from router to the pi. And also keep in mind that the Mac has to be on the same

network.

Now we have our IP address of the Pi. We can use mac’s terminal to SSH into the PI.

Open terminal and enter the command

ssh pi@192.168.94

Now press enter.

Types yes and press enter.

The password was set to “raspberry”. As you type in the password you will see no

characters. Once the password is completed press enter and you will be logged into

raspberry pi console.

Now we can enable VNC viewer to have Desktop GUI access.

Type the command

sudo raspi-config

And press enter this will direct to raspberry pi configuration.

Go to interface options

Go to VNC, enable the VNC Server by choosing Yes. Then go to Display options. Then

VNC Resolution and select 1280x720. Once that is done, click on tab and finish it, when

asked for reboot select yes.

After this the SSH session will end on Terminal. Now let’s install VNC viewer. Go to

(https://www.realvnc.com/en/connect/download/viewer/)

Click on Download VNC Viewer. Once the DMG file is downloaded open it.

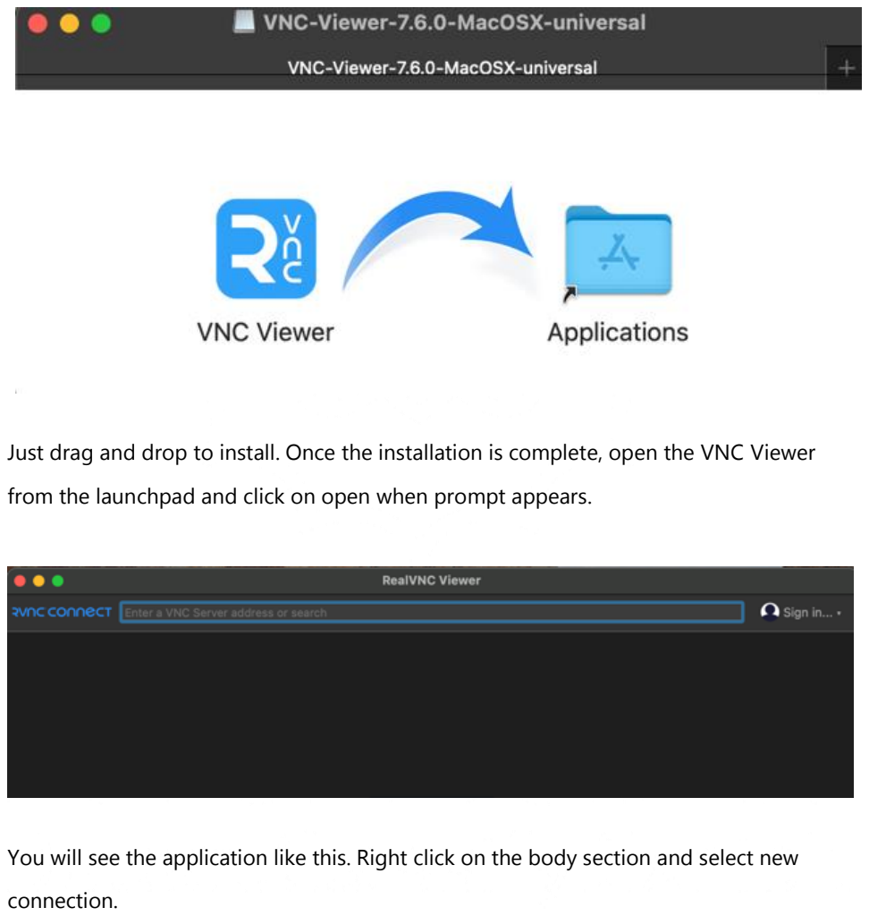
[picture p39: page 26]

Just drag and drop to install. Once the installation is complete, open the VNC Viewer

from the launchpad and click on open when prompt appears.

You will see the application like this. Right click on the body section and select new

connection.

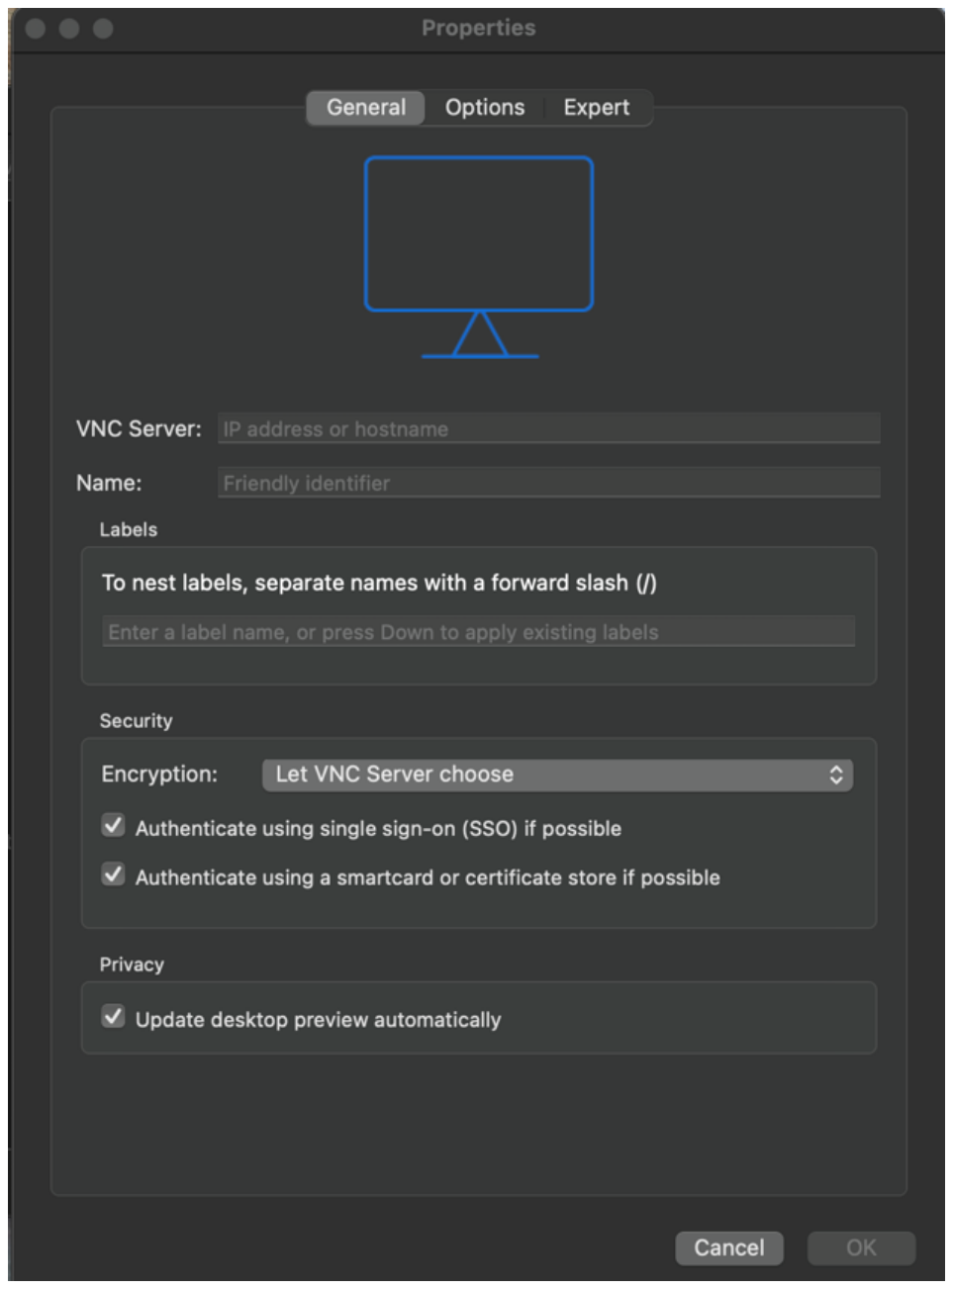
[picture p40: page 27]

In VNC Server we have to input the IP address of the Pi. (192.168.1.94) and the name can

be anything (Pi).

Click on Ok.

This icon will appear, double click on it.

A prompt will appear, click on Continue.

Username is “pi” and the password is “raspberry”. Check the remember password box

and click ok.

The Raspberry pi desktop will appear and we can use raspberry pi now. The warning can

be closed by clicking on ok.

SSH and VNC only works locally and are often time consuming because whenever the IP

changes then the whole thing has to be reconfigured. So, we can use third party

application like any desk, TeamViewer for easy access. Whenever the device is

connected to the internet, no matter from where, they can be configured once to be

logged in using the same credentials.

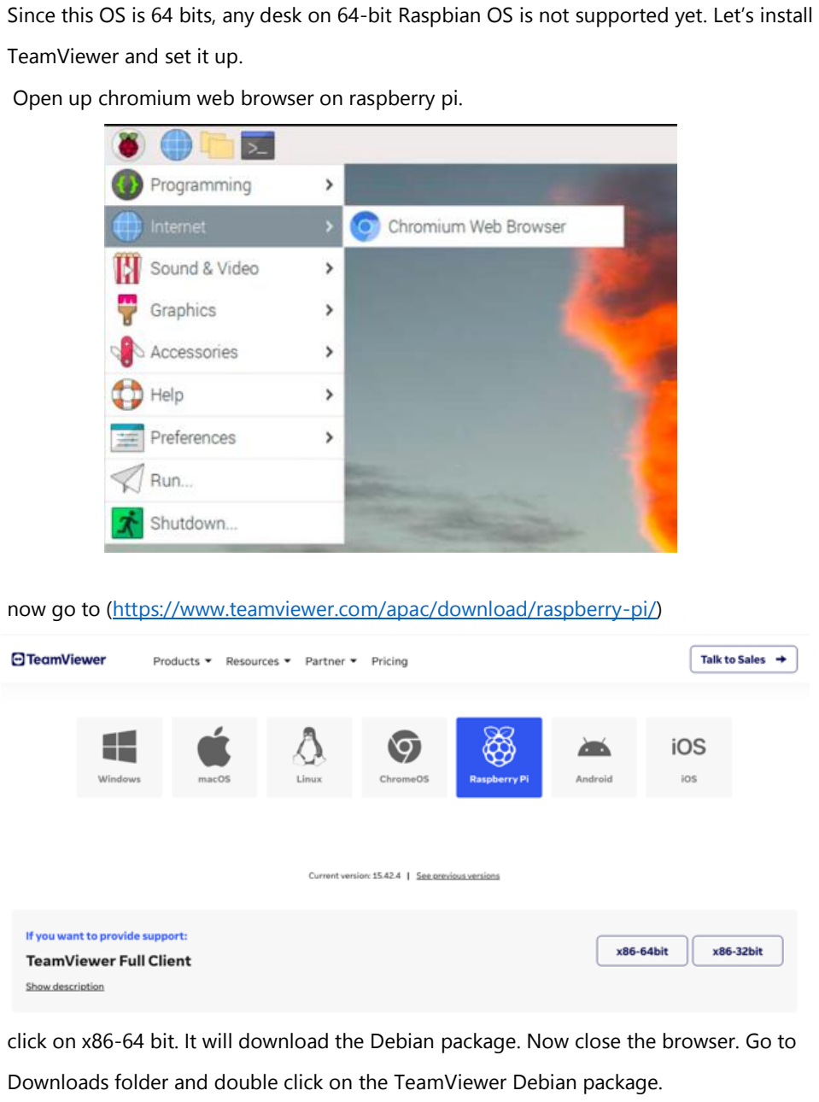
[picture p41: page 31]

Since this OS is 64 bits, any desk on 64-bit Raspbian OS is not supported yet. Let’s install

TeamViewer and set it up.

Open up chromium web browser on raspberry pi.

now go to (https://www.teamviewer.com/apac/download/raspberry-pi/)

click on x86-64 bit. It will download the Debian package. Now close the browser. Go to

Downloads folder and double click on the TeamViewer Debian package.

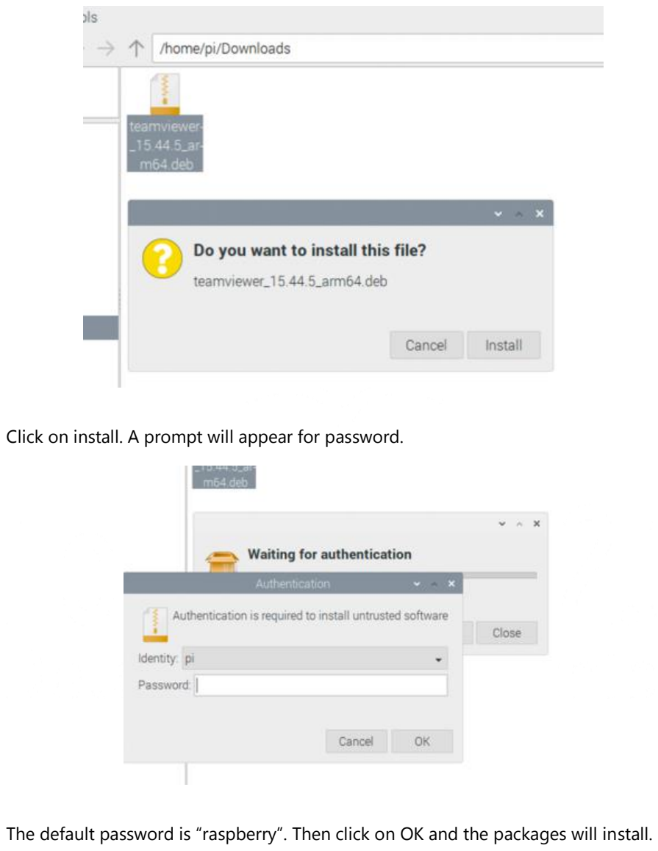
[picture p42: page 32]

Click on install. A prompt will appear for password.

The default password is “raspberry”. Then click on OK and the packages will install.

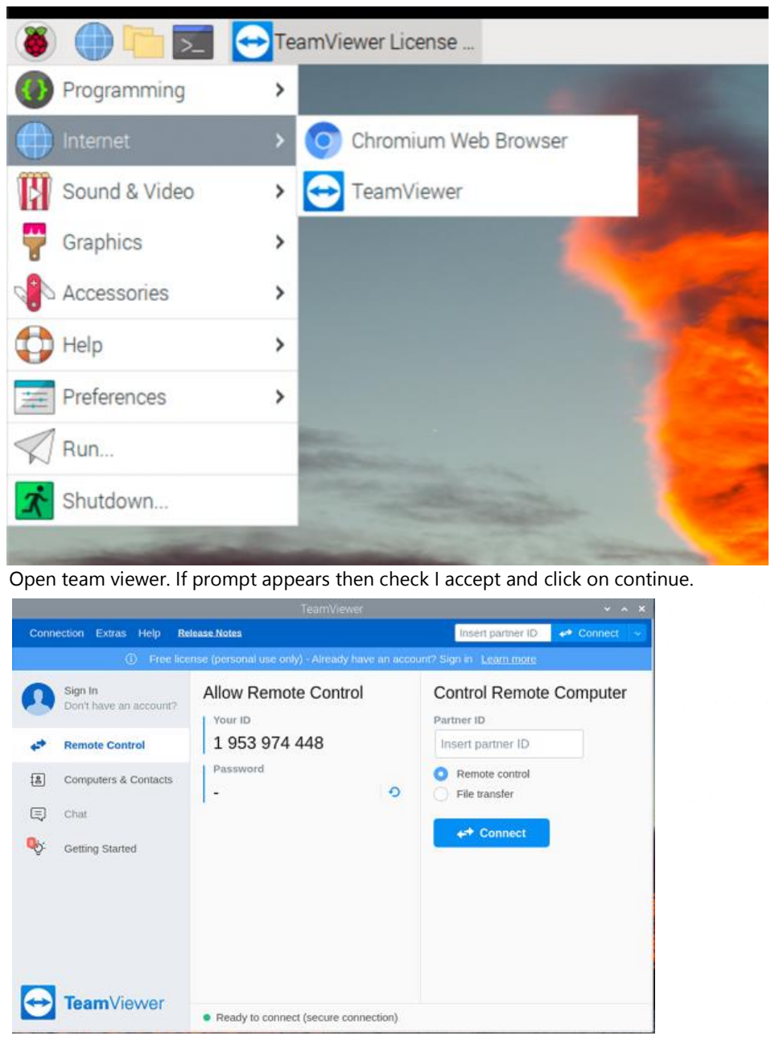
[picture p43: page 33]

Open team viewer. If prompt appears then check I accept and click on continue.

This screen will appear.

Let’s setup it in such a way that the password remains the same and TeamViewer always

runs at boot.

Go to extras then options. In general check the start TeamViewer with system.

Go to Security tab and disable random password.

Go to advanced and then under Personal password, keep a password of your choice.

Click on Apply and Ok.

Now we can install team viewer in the mac and try to access the pi using the id and

password we got from above steps.

Go to (https://www.teamviewer.com/apac/download/macos/) from browser in mac.

Click on Download in TeamViewer full client. Once download is complete, open the file.

Double click on the icon and a prompt will appear click on Open. Another prompt will

appear click on I accept and continue.

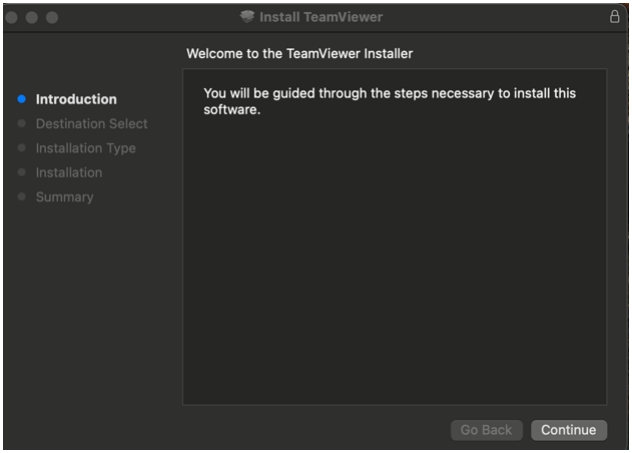
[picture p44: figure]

The installation process will begin. Follow the instruction and install team viewer. Once

the installation is complete, open TeamViewer from launchpad.

Then you can use the Id and password we set from above steps and we can access our

pi easily.

Hardware needed:

https://thepihut.com/products/raspberry-pi-4-model-b?variant=20064052740158&src=raspberrypi

https://thepihut.com/products/adafruit-aht20-temperature-humidity-sensor-breakout-board (optional)

https://thepihut.com/products/adafruit-tsl2591-high-dynamic-range-digital-light-sensor (optional)

https://thepihut.com/products/adafruit-mini-gps-pa1010d-uart-and-i2c-stemma-qt (optional)

(NHBS, 2023)

The Ultramic is a fully digital USB ultrasound microphone with integrated digital to analog converter and an option of 192 kHz, 200kHz or 250kHz sampling rate. The USB 2.0 port allows for easy connection to your PC or MAC and no driver installation is required.

Compact and versatile the Ultramic is a great option for use in the field or laboratory. Whilst most often used to record the ultrasonic signals of both bats and rodents it is equally useful for detection of high-frequency noises emitted by LCD screens, turbines and power adaptors.

Specification

* 192K, 200K or 250K sampling per second.
* True 16 bit resolution.
* Frequency range up to 100kHz - 125kHz.
* MEMS high sensitivity Surface Mount Wide-band Ultrasonic Acoustic Sensor. * High quality and low noise analogue amplification.
* USB full speed port with a mini B USB connector.
* 32 bit 80MHz integrated microcontroller.
* Dimensions: 130mm length x 20mm diameter.

Available on https://www.nhbs.com/ultramic-usb-ultrasound-microphone

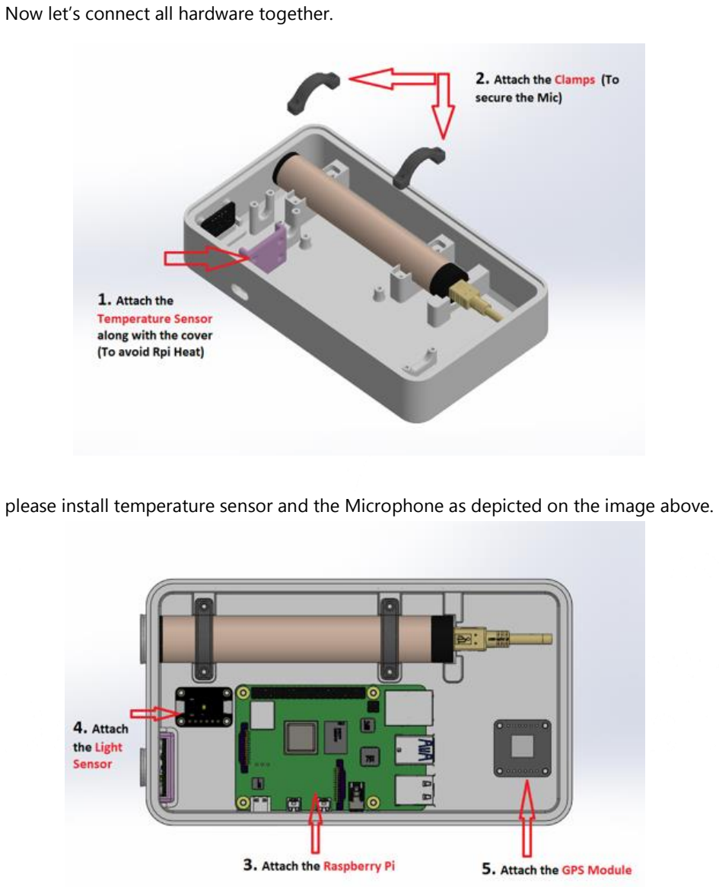
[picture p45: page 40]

Now let’s connect all hardware together.

please install temperature sensor and the Microphone as depicted on the image above.

Then we can place light sensor, GPS module and Raspberry Pi inside the housing. Power

supply is connected to Pi via a cut out from the side. The microphone is connected on

the USB port.

All three sensors are STEMMA QT / Qwiic compatible. The sensor can be wired from one

to another in a daisy chain.

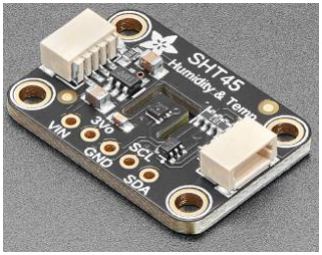
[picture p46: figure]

The white connectors on the side in the above SHT45 temperature and humidity sensors

are STEMMA QT / Qwiic connectors. Qt cable can be directly connected on those ones.

Please use

STEMMA QT / Qwiic JST SH 4-pin Cable with Premium Female Sockets as in the pictures

below.

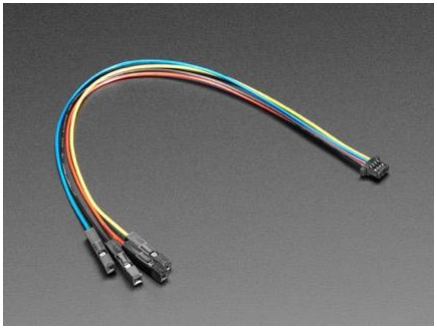
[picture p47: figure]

The connector side is connected to the sensor and the female sockets are connected to

the raspberry pi’s GPIO pin.

The female socket cables are color coded so they can be easily used. The red-wire is

VCC, black wire is GND, blue is SDA and yellow is SCL.

Red wire: | pin 1 of raspberry pi (3v3)
Black wire: | pin 6 of raspberry pi (GND)
Blue wire: | pin 3 of raspberry pi (GPIO 2) (SDA)

Yellow wire: pin 5 of raspberry pi (GPIO 3) (SCL)

After that we use QT to QT cable ( STEMMA QT / Qwiic JST SH 4-Pin Cable - 200mm

Long ) to connect between sensors as shown in figure below.

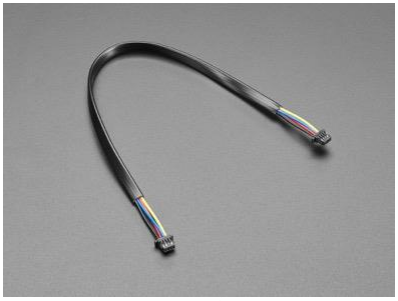
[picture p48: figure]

The final result should look like this. The pi

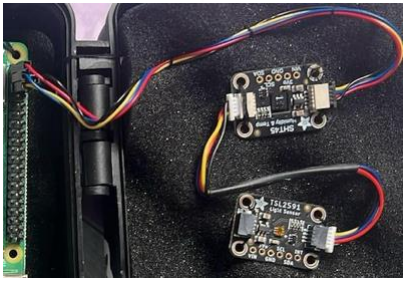
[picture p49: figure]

Likewise, GPS module is also connected in similar fashion. Now all the hardware is

connected and assembled. Let’s start programming them to test and build it completely.

All the sensors are I2C. Let’s enable I2C on raspberry pi.

Go to application menu, then preferences then Raspberry Pi configuration.

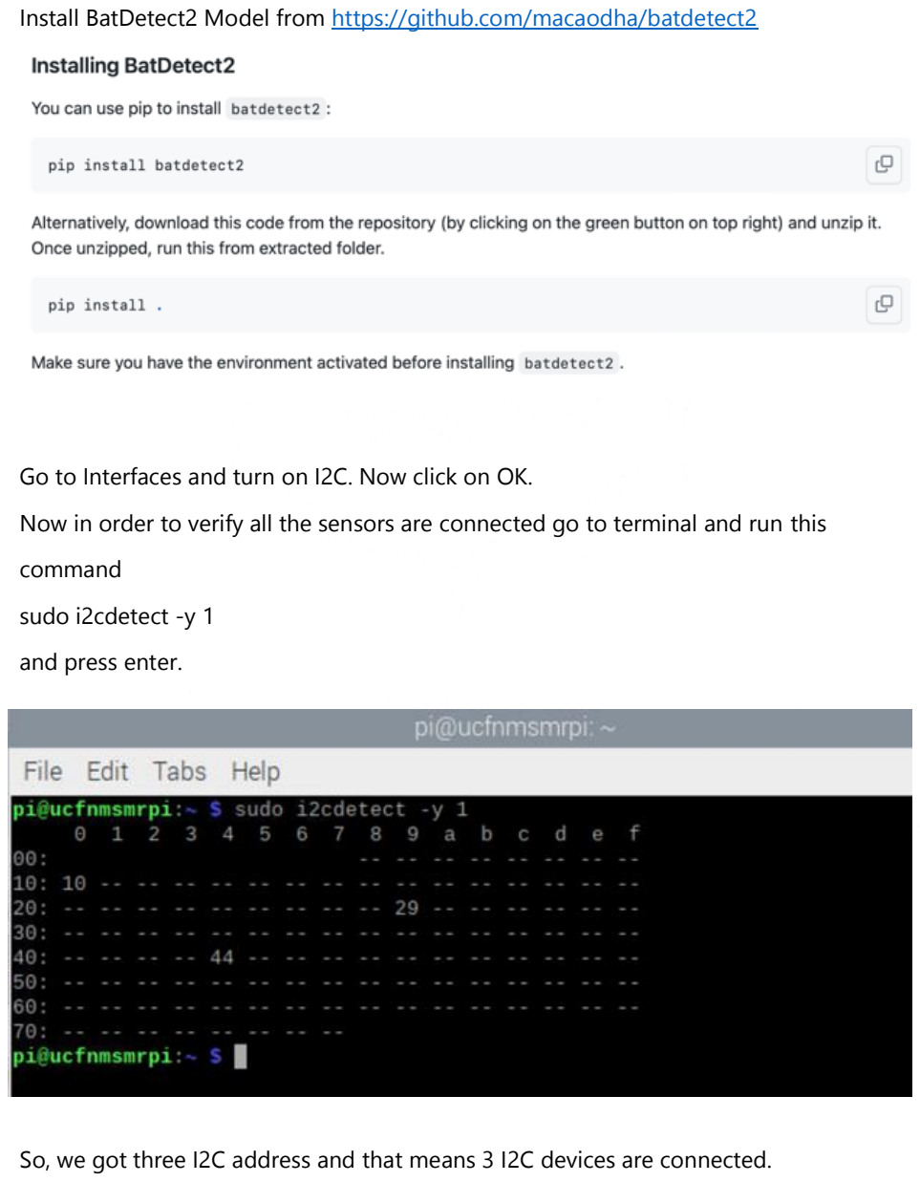
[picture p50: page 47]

Install BatDetect2 Model from https://github.com/macaodha/batdetect2

Go to Interfaces and turn on I2C. Now click on OK.

Now in order to verify all the sensors are connected go to terminal and run this

command

sudo i2cdetect -y 1

and press enter.

So, we got three I2C address and that means 3 I2C devices are connected.

Now let’s install libraries for all three sensors.

In order to install library for SHT45 sensor, run the following command.

sudo pip3 install adafruit-circuitpython-sht4x

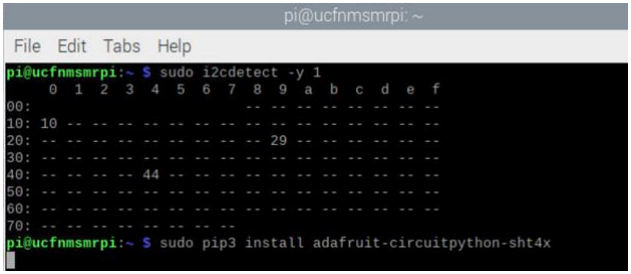
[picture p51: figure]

once the library is installed you should be able to see this screen.

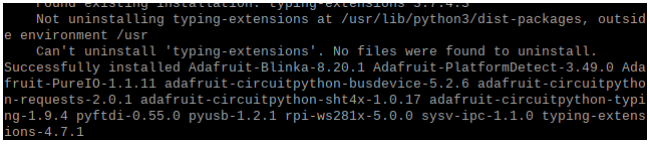
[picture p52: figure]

Now let’s run the test code and check the output. Let’s create a python file in desktop

and paste this code there are run.

Let’s run the code and check the output.

Temperature and humidity were obtained in the serial monitor.

Now let’s install library for light intensity sensor. In order to install library for TSL2591

sensor, run the following command

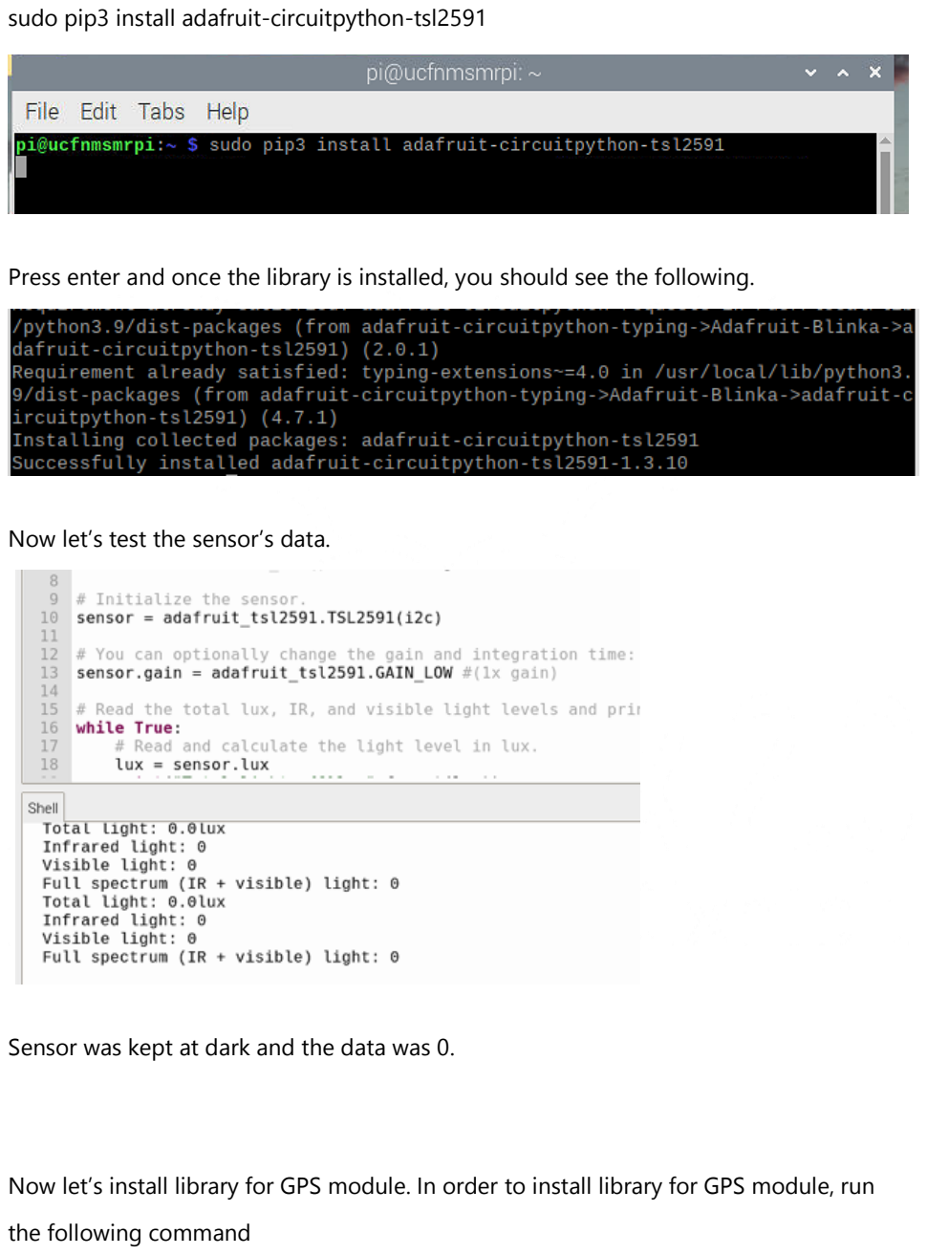
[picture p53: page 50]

sudo pip3 install adafruit-circuitpython-tsl2591

Press enter and once the library is installed, you should see the following.

Now let’s test the sensor’s data.

Sensor was kept at dark and the data was 0.

Now let’s install library for GPS module. In order to install library for GPS module, run

the following command

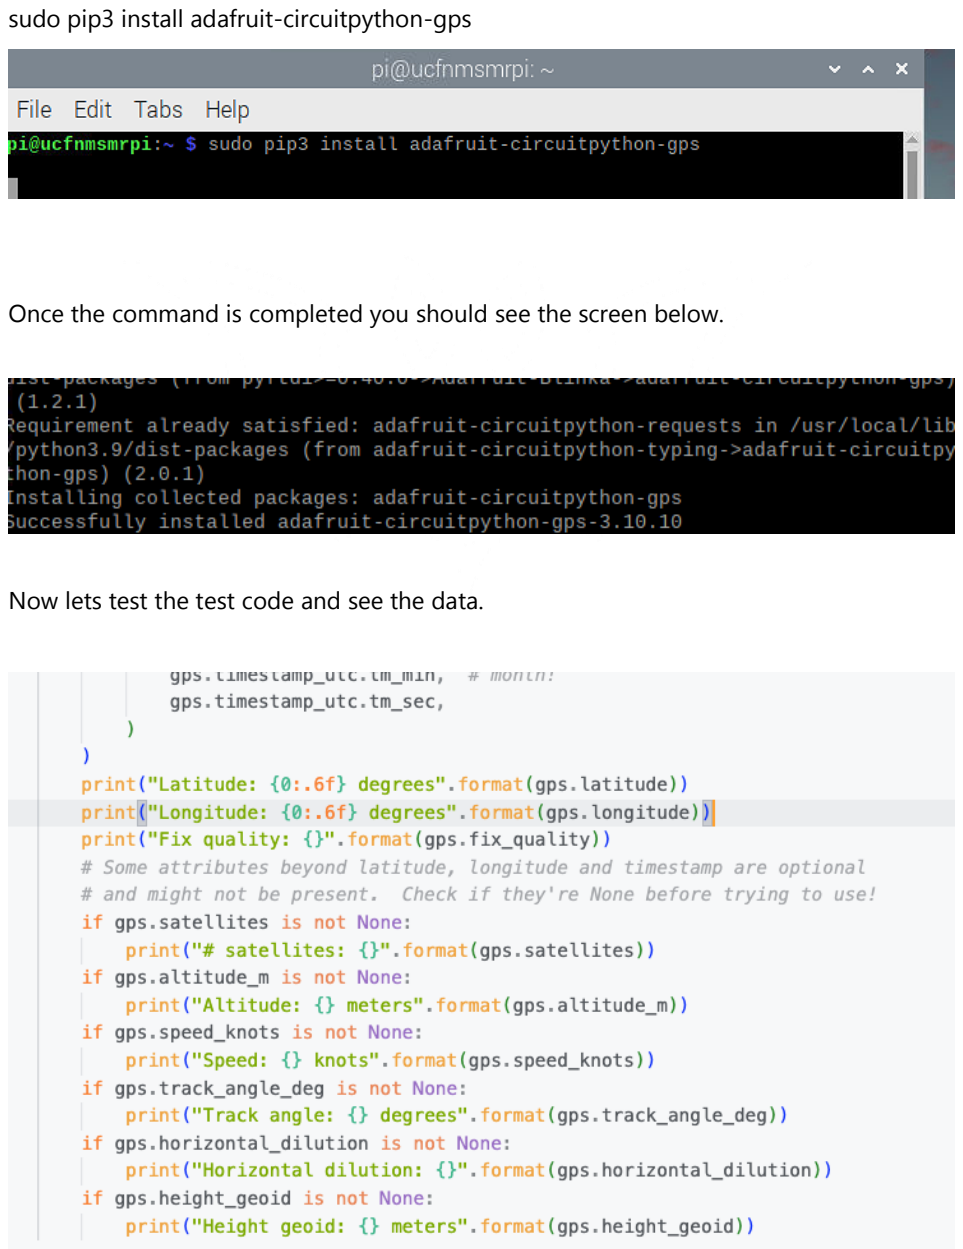
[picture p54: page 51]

sudo pip3 install adafruit-circuitpython-gps

Once the command is completed you should see the screen below.

Now lets test the test code and see the data.

The above is just a snippet of the test script.

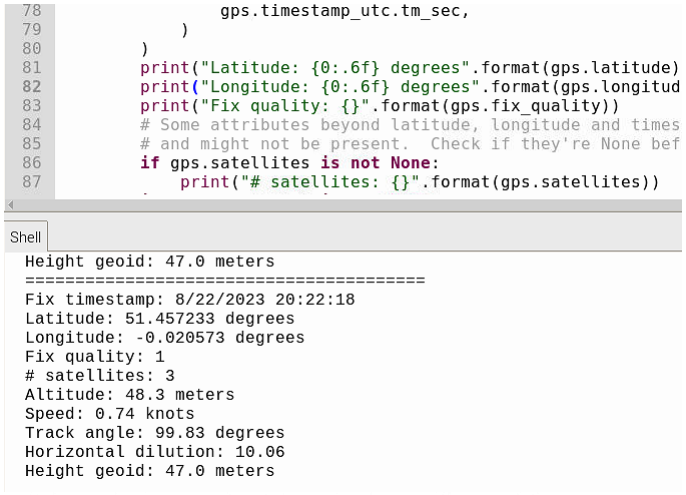
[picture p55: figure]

we could get the data of the GPS coordinates and all other data.

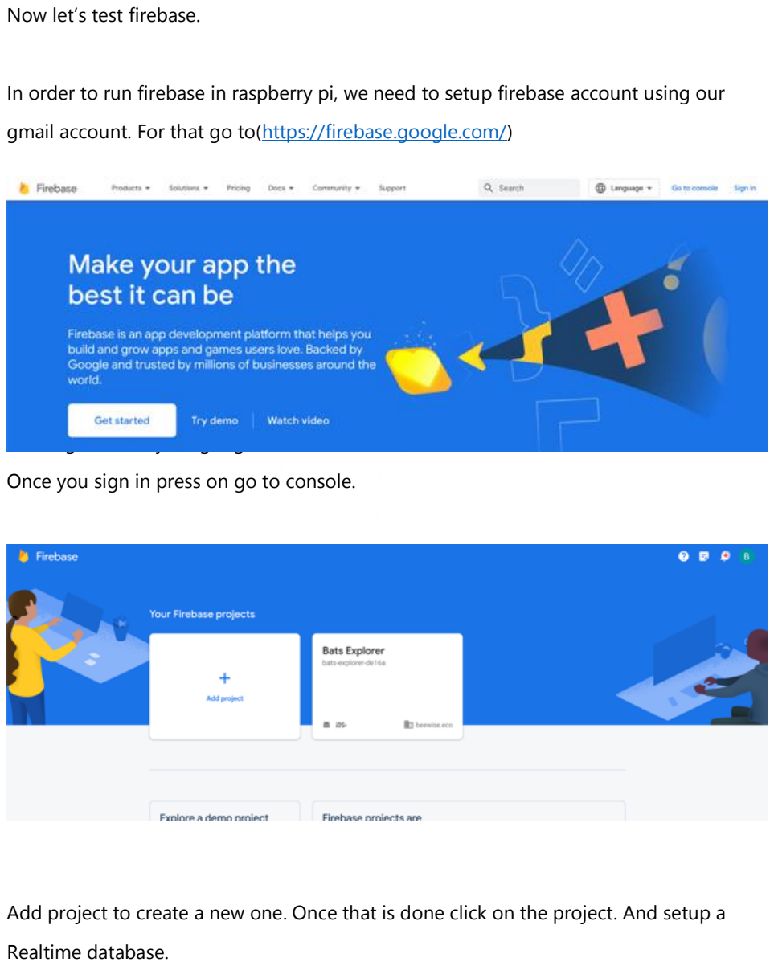
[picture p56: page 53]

Now let’s test firebase.

In order to run firebase in raspberry pi, we need to setup firebase account using our

gmail account. For that go to(https://firebase.google.com/)

Now sign in with your google account.

Once you sign in press on go to console.

Add project to create a new one. Once that is done click on the project. And setup a

Realtime database.

Now we need config parameters from the fire, you can get databaseURL from realtime

database, apiKey from Project settings and authDomain and storageDomain from user

uid inside authentication.

Now let’s use this info and send data from raspberry pi to the firebase.

Let’s install the library we need to send data to firebase.

sudo pip3 install pyrebase

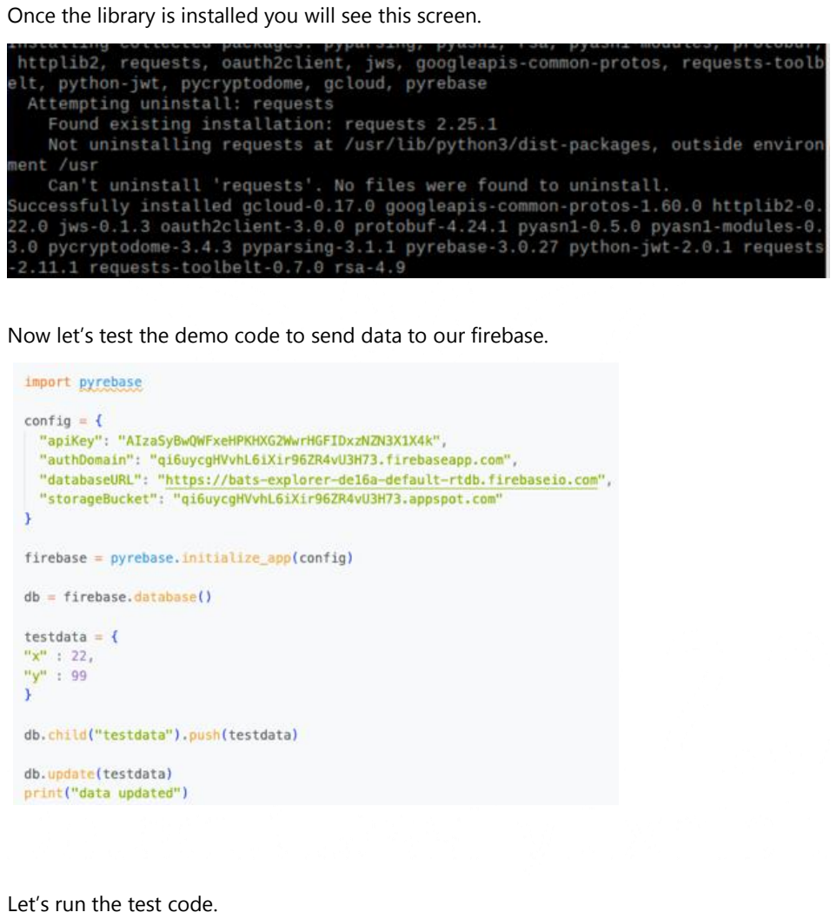
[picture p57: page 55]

Once the library is installed you will see this screen.

Now let’s test the demo code to send data to our firebase.

Let’s run the test code.

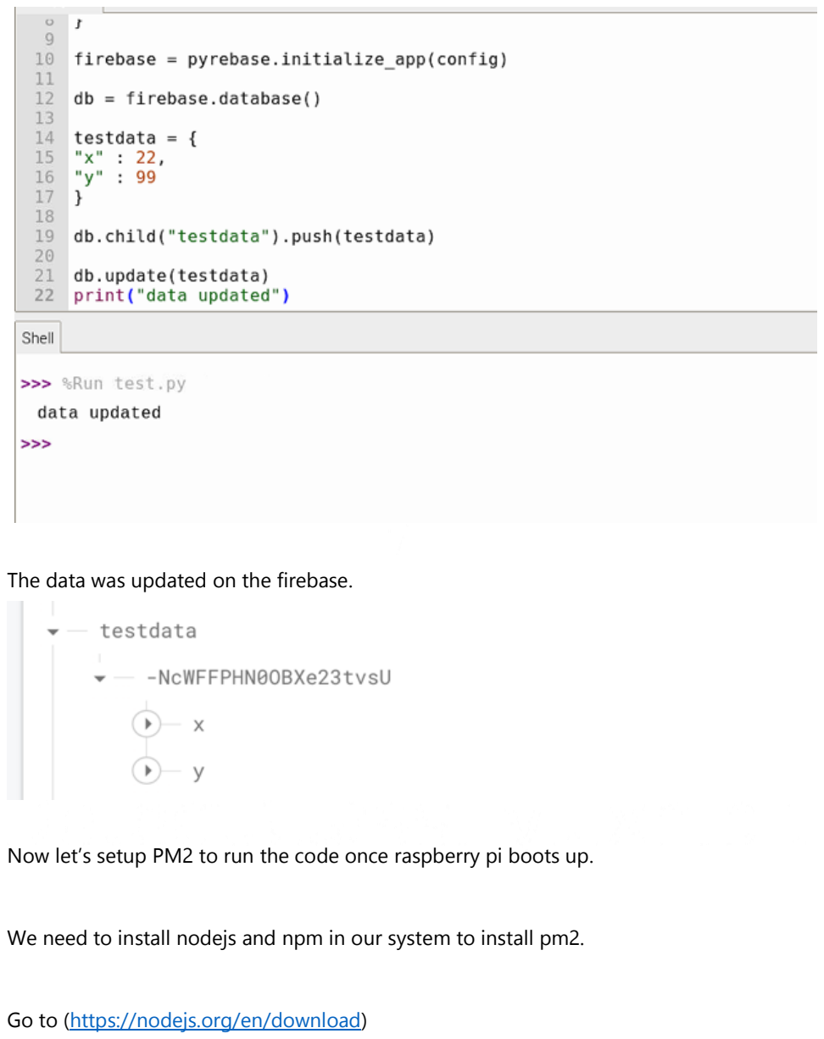
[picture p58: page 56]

The data was updated on the firebase.

Now let’s setup PM2 to run the code once raspberry pi boots up.

We need to install nodejs and npm in our system to install pm2.

Go to (https://nodejs.org/en/download)

Now we copy link for Linux binary(arm) ARMv8 because our raspberry pi has 64-bit OS.

Then we run this command

wget https://nodejs.org/dist/v18.17.1/node-v18.17.1-linux-arm64.tar.xz

Once the package is downloaded extract that.

Copy the Extracted Files to Directory Path.

To do that go to terminal and type

cd node-v18.16.1-linux-arm64

now run

sudo cp -R * /usr/local

Once the process completes it will go to next line on terminal.

Now let’s verify npm and node

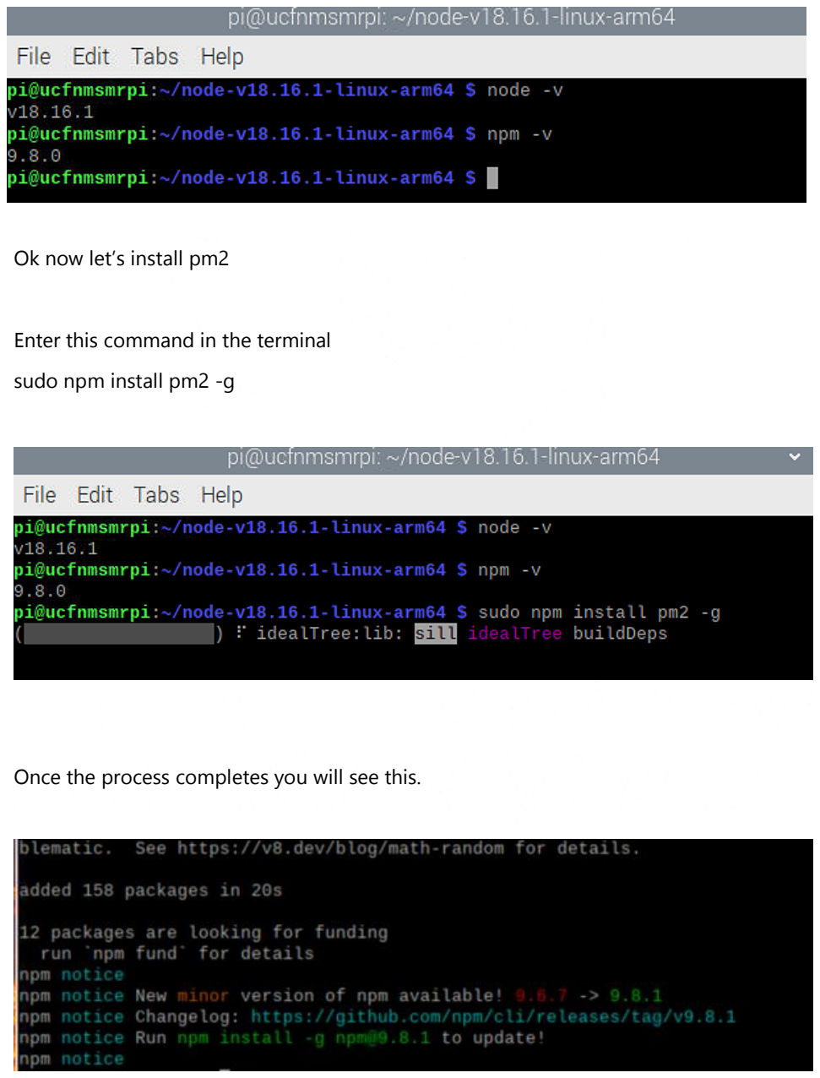
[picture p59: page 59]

Ok now let’s install pm2

Enter this command in the terminal

sudo npm install pm2 -g

Once the process completes you will see this.

Now let’s finalize our final codes and place them in Raspberry pi and run the automated

scripts.

The temperature/humidity sensor’s code, firebase’s code was compiled together and

saved in Final.py

The GPS sensor’s code, firebase’s code was compiled together and saved in gpsFinal.py

To automate this scripts, we went to terminal and ran this command.

pm2 start Final.py –interpreter python3

And the same for gpsFinal script

pm2 start gpsFinal.py –interpreter python3

Then we ran

pm2 save

Now in order to run these scripts once Raspberry pi turns on. let’s run the scripts in

startup.

To do that run this command in terminal.

sudo pm2 startup

after this the code was able to run at boot. So, we rebooted.

To verify automatic starting of the code we ran

pm2 list

We could see that the scripts were running and the data was also being sent to the

firebase.

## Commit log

2023-08-21 Create GPS Sensor Code
2023-08-21 Update GPS Sensor Code
2023-08-22 Create Enclosure Design
2023-08-22 Update Enclosure Design
